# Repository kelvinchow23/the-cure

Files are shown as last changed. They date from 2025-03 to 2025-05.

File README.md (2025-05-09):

# the cure - a UV curing module for well plates



## Purpose
The main function of the curing module is for photopolymerization of a sample using a [UV flood lamp](https://www.amazon.ca/Everbeam-365nm-50W-Black-Light/dp/B08635F9CX/?th=1), intended for samples in a well plate. 
Since UV light poses safety risks, the module includes a motorized tray that slides in and out of a fully enclosed housing. This shields users and the surrounding environment from exposure during operation.
The module is intended to integrate into an automated workflow where a robot arm can pick and place well plates into the box for curing.

## Requirements
- **Microcontroller:** Raspberry Pi Pico W running MicroPython. Honestly, the firmware is very simple and can be adapted to other controllers. It's a matter of controlling 2 digital IO pins for turning on/off relays.
- **Host Computer:** Required to upload firmware and communicate via USB serial. The Pico could potentially operate standalone (e.g., over MQTT), but you’ll still need a computer to flash it initially.
- **Power Source:** Build instructions are for 120VAC (standard NEMA 5-15 plug).
- **Lamp:** The UV lamp has an on/off switch — make sure it is switched *on* for operation.

## Build Overview

This repository includes a three-part guide:
1. **Electronics:** Build and test the electrical components. Instructions are in the `/electrical` folder. 
2. **Mechanical Assembly:** Build instructions for the mechanical housing are in the `/mechanical` folder. 
3. **Firmware & Control:** Use the provided scripts (or your own) to control the module. See **Module Operation** below for operation. 

## Module Operation

The `/scripts` folder contains two key scripts.  
The main firmware script, `UV_module.py`, is uploaded to the microcontroller and provides three core functions:

1. **`move_wellplate_out()`** – Extends the well plate tray.
2. **`move_wellplate_in()`** – Retracts the well plate tray.
3. **`turn_on_UV(duration)`** – Turns on the UV lamp for a specified duration (in minutes).

These functions can be called directly from the microcontroller or remotely via a host computer using tools like `mpremote`.

The `UV_module_controller.py` script is designed to be run on a host computer.  
It communicates with the microcontroller over a serial COM port (currently set to `COM4`, but this may need to be updated based on your system).

When executed, the current workflow is as follows:
1. Retract the well plate tray.
2. Cure the sample for 30 seconds.
3. Extend the well plate tray.

## Notes
- Most 3D-printed parts are made from ASA filament, which is more UV-resistant than standard materials. If ASA printing isn't available, use an alternative UV-resistant material for the housing.
- The actuator's 200mm extension matches the UV lamp’s length (~8"). If using a different lamp, adjust the actuator and tray length to suit.  Note that the guide drawer slides must have an extension longer than the actuator's extension. In this case, the drawer slides have an 8" [203.2mm] extension length.
- This module was designed to mount to an M6 breadboard table. If mounting elsewhere, change the hole features in the UVouter base [C5]. STEP and fusion files are [here](https://github.com/kelvinchow23/the-cure/tree/main/mechanical/3D%20prints%20and%20CAD%20files).

---
  
## Future Steps
- **Electronics:** swap out the perfboard electronics with something a bit cleaner.  it's currently using a dpdt relay since the actuonix actuators were intended to use without an external conntroller. I think this can be done cleaner with an H-bridge module or a 2-channel SPDT relay module. It would still be necessary to have the 3rd relay for controlling the lamp.
- **Housing:**.  The outer and inner housing can be merged together.  This was initially done in two steps because initially, there was no thought of how the moudule would be fixed to a table.
- **UV Lamp:** The lamp itself is not characterized well apart from knowing the wavelength.  Intensity and spatial distribution isn't well known. 
- **Mechanical Housing:** Simplify the housing. The base can likely be reduced from two parts to one. Originally, the two-piece base was added to allow mounting to a plate, which might now be unnecessary with design tweaks.

## Revision History
- **Revision A** - Updated: 2025-04-14

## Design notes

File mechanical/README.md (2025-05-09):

## Bill of Materials (BOM)
Refer to the spreadsheet for the full bill of materials. 
- Parts starting with B need to be purchased. 
- Parts starting with C need to be 3D printed (see below for images of the parts). These parts can be found in the [3D prints and CAD files folder](https://github.com/kelvinchow23/the-cure/tree/main/mechanical/3D%20prints%20and%20CAD%20files).
- The part starting with D needs to be assembled (see instructions in the [electrical folder](https://github.com/kelvinchow23/the-cure/tree/main/electrical)).

### 3D Printed Parts

| #   | Part Name               | Part Qty | Revision | Material | Notes                                                   | Picture Link                                          |
|-----|--------------------------|----------|----------|----------|---------------------------------------------------------|-------------------------------------------------------|
| C1  | Tray                     | 1        | A        | ASA      |  4X M4 heat sets, 4X M3 heat sets                       |   |
| C2  | Actuator Bracket          | 1        | A        | PLA      | Print with any filament, 5X M4 heat sets                |  |
| C3  | Tray Insert              | 1        | A        | ASA      |                                                         |   |
| C4  | Electronics Mounting Plate| 1        | A        | PLA      | Print with any filament, 6X M3 heat sets                | |
| C5  | UV Outer Base            | 1        | A        | ASA      | This is big, split if necessary                        ||
| C6  | Shield                   | 1        | A        | ASA      |                                                       |   |
| C7  | UV Base Lid              | 1        | A        | ASA      |                                                         | |
| C8  | UV Inner Base            | 1        | A        | ASA      | 12X M4 heat sets, 4X M3 heat sets                      | |
| C9  | Back Connector Panel     | 1        | A        | ASA      | 1X M4 heat sets, 2X M3 heat sets                       |  |

*ASA is more UV resistant. Non-ASA parts can be printed with any filament.*

## Tools
- Soldering iron (for soldering and heat sets)
- screwdrivers
- Allan keys
- adjustable wrench
- wire stripper/cutter/crimper
- multimeter
- computer to upload scripts

## Assembly Instructions

Refer to the assembly insturctions document for the build guide.

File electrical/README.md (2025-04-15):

# ⚡ Electrical Components Testing

Before assembling the box, it's a good idea to verify that the electronics function as expected. There are two output devices to test:

1. **Linear Actuators**  
   Verify that the two actuators can extend and retract, and that they are controllable via a GPIO pin on a microcontroller.

2. **AC Relay**  
   Confirm that the AC relay clicks (indicating switching) when triggered by a GPIO pin from a microcontroller.

---

## 🧾 Bill of Materials (BOM)

| #    | Part Description                    | QTY | Vendor   | Vendor/Mfr Part #       | Notes / Link                                                              |
|------|-------------------------------------|-----|----------|--------------------------|---------------------------------------------------------------------------|
| A1   | Raspberry Pi Pico WH (RP2040)       | 1   | Digikey  | SC0919                   | Could substitute with another microcontroller                            |
| A2   | DPDT Relay, 12V, 5V Coil            | 1   | Digikey  | J104B2C12VDC.15S         | Also available from Actuonix (same part)                                 |
| A3   | NPN Transistor                      | 1   | Digikey  | TIP120                   | Interchangeable with similar-rated parts                                 |
| A4   | Flyback Diode                       | 1   | Digikey  | 1N4004G-T                | Interchangeable with similar-rated parts                                 |
| A5   | 1kΩ Resistor                        | 1   | Digikey  | -                        | Interchangeable with similar-rated parts                                 |
| A6   | Header Pins, 0.1" Pitch             | 9   | Digikey  | PRPC040SACN-RC           | Interchangeable with similar-rated parts                                 |
| A7   | 3.2" x 2" Protoboard                | 1   | Digikey  | DKS-SOLDERBREAD-02       | —                                                                         |
| A8   | AC Relay (3.3V Coil)                | 1   | Digikey  | 103020005                | Interchangeable with similar-rated parts                                 |
| A9   | Grove 4-Pin Female Jumper           | 1   | Digikey  | 110990028                | —                                                                         |
| A10  | 100mm Stroke Linear Actuator, 12VDC | 2   | Actuonix | L16-100-63-12-S          | [Link](https://www.actuonix.com/l16-100-63-12-s)                          |
| A11  | 12VDC Power Supply                  | 1   | Actuonix | dcpowersupply            | Can use alternative 12V supply for testing                                |
| A12  | USB Micro-B to USB-A Cable          | 1   | Digikey  | DH-20M50057              | Interchangeable with similar-rated parts                                 |

---

## 🧰 Wiring Diagram

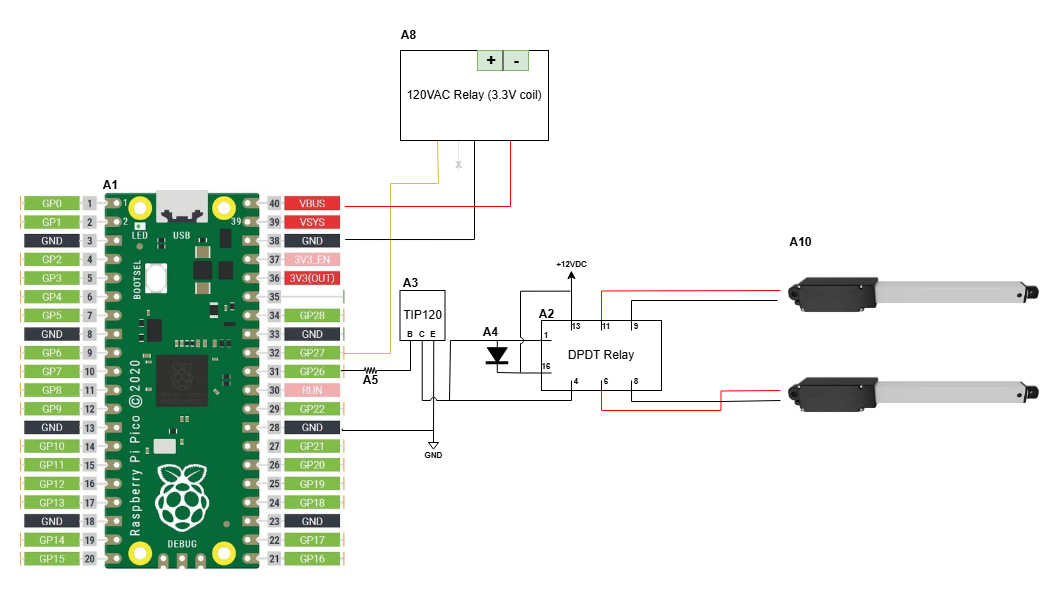
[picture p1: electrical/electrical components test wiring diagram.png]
Wiring Diagram
  
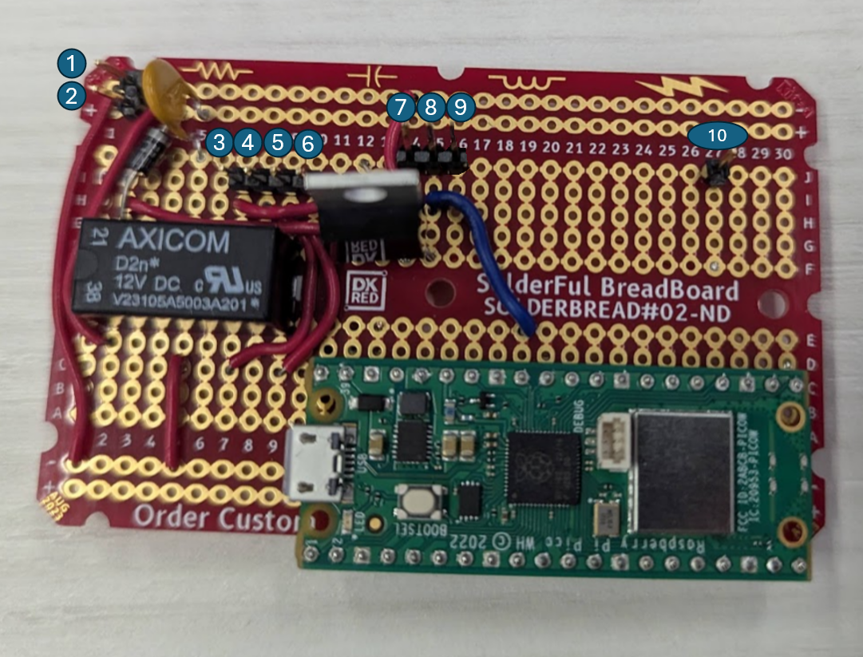
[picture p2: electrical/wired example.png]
Physical Example


- The diagram outlines the setup. The two relays—DC (for actuators) and AC (for a lamp)—can be tested independently.
- You don't need to connect the output terminals of the AC relay yet; a click is sufficient for now.
- A fuse is shown in the diagram connecting V+ to the relay. You can replace this with a jumper wire for testing.
- Wiring on the underside of the protoboard may not be visible in the physical photo.

---

## 🧪 Build & Test Instructions

1. Gather the components listed in the BOM. Substitutes are generally acceptable.
2. Solder components **A1–A6** onto the **A7** protoboard, following the wiring diagram.
   - **Pins 1–2**: 12V Power Supply (V+ and GND)
   - **Pins 3–6**: Actuator outputs (reverse polarity to change direction)
   - **Pins 7–9**: Grove connector to external relay
   - **Pin 10**: external 5V power input (not required if the pico is powered via USB. This will be necessary if it's a standalone module)
3. Connect the linear actuators to pins 3–6. Confirm they move **together**.
4. Connect the AC relay module to pins 7–9 via the Grove jumper. The white cable is not connected.
5. Power the board with a 12V supply through pins 1–2.
6. Connect the Raspberry Pi Pico to your computer using the USB cable.
7. Flash the Pico with **MicroPython firmware**.
8. Upload and run the script `the_cure_electrical_test.py`.
9. The test script will run the following loop:
   - a. Extend actuators  
   - b. Delay: 15 seconds  
   - c. Retract actuators  
   - d. Delay: 10 seconds  
   - e. Turn relay ON (click)  
   - f. Delay: 5 seconds  
   - g. Turn relay OFF  
   - h. Delay: 3 seconds

✅ If the actuators cycle correctly and you hear the relay click, the electronics are working. You can now proceed with the mechanical assembly.

> ⚠️ If actuators **start by retracting**, reverse their polarity or adjust the code.

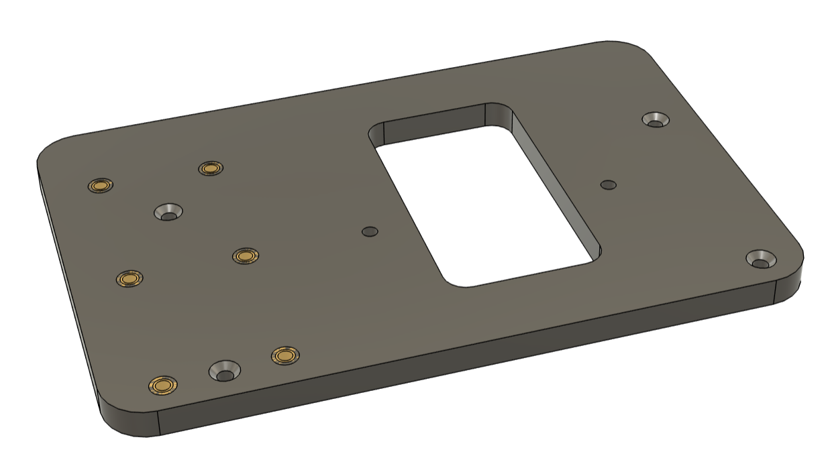
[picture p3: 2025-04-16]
mechanical/3D prints and CAD files/png/electronics mounting plate RevA.png

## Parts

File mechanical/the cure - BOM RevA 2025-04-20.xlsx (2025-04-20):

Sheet: the cure BOM
the cure BOM
Purchased Parts
# | Part Name | Quantity | Vendor | Vendor/Mfr Part # | Unit Cost (USD) | Unit Cost (CAD) | Total Cost (CAD) | Notes
B1 | #8-32 BH screw, 5in L, steel | 1 | McMaster Carr | 90272A053 | $1.05 | $1.51 | $1.51
B2 | M3 BH screw, 6mm L, SS | 4 | McMaster Carr | 92095A179 | $0.06 | $0.08 | $0.34
B3 | M4 BH screw, 6mm L, SS | 18 | McMaster Carr | 92095A188 | $0.12 | $0.17 | $3.14
B4 | M3 FH screw, 10mm L, SS | 6 | McMaster Carr | 92125A130 | $0.07 | $0.11 | $0.63
B5 | M3 standoff, 10mm L, M-F, nylon | 8 | McMaster Carr | 95783A001 | $2.49 | $3.59 | $28.68
B6 | M3 BH screw, 10mm L, SS | 2 | McMaster Carr | 92095A182 | $0.07 | $0.10 | $0.21
B7 | M4 set screw, 6mm L, steel, nylon tip | 4 | McMaster Carr | 94095A110 | $1.72 | $2.48 | $9.91
B8 | M3 FH screw, 6mm L, SS | 2 | McMaster Carr | 92125A126 | $0.06 | $0.09 | $0.18
B9 | M3 FH screw, 20mm L, SS | 4 | McMaster Carr | 92125A136 | $0.13 | $0.19 | $0.74
B10 | M4 BH screw, 10mm L, SS | 4 | McMaster Carr | 92095A190 | $0.09 | $0.14 | $0.54
B11 | M4 BH screw, 15mm L, SS | 1 | McMaster Carr | 92095A125 | $0.09 | $0.13 | $0.13
B12 | M4 to #8-32 thread adapter, 1.5in L, steel | 1 | McMaster Carr | 91082A110 | $11.57 | $16.66 | $16.66
B13 | Cable tie mount, 19mm base, nylon | 1 | McMaster Carr | 7566K104 | $0.08 | $0.12 | $0.12
B14 | M4 locknut, 316 SS, nylon insert | 1 | McMaster Carr | 94205A230 | $0.15 | $0.21 | $0.21
B15 | threadlocker, medium strength | A/R | McMaster Carr | 91458A112 | $0.00 | $0.00 | $0.00
B16 | UV flood lamp, 365nm, 50W | 1 | Amazon | B08635F9CX | $0.00 | $59.99 | $59.99 | https://www.amazon.ca/Everbeam-365nm-50W-Black-Light/dp/B08635F9CX/?th=1
B17 | Drawer slides, 8in, pair | 1 | Amazon | B08VD84GV9 | $0.00 | $14.99 | $14.99 | https://www.amazon.ca/Laigoo-Extension-Bearing-Cabinet-Drawers/dp/B08VD84GV9
B18 | 5/12V dual power supply | 1 | Digikey | 1866-3983-ND | $0.00 | $16.89 | $16.89
B19 | USB-micro B cable, panel mount, 1ft | 1 | Digikey | 1528-1786-ND | $0.00 | $4.95 | $4.95
B20 | Power entry connector, C14, Panel mount | 1 | Digikey | 486-1963-ND | $0.00 | $10.47 | $10.47
B21 | cable ties | A/R | Digikey | 2162-AL-04-18-9-M-ND | $0.00 | $0.00 | $0.00
B22 | M3 heat set inserts | 20 | Digikey | 2254-M30X170C-ND | $0.00 | $0.34 | $6.80
B23 | M4 heat set inserts | 22 | Digikey | 5519-TH-M40-SV-ND | $0.00 | $0.16 | $3.52
B24 | Linear actuators, L-16-S, 63:1, 100mm stroke | 2 | Actuonix | L16-100-63-12-S | $70.00 | $100.80 | $201.60
B25 | Actuator mounting bracket | 1 | Actuonix | - | $0.00 | $0.00 | $0.00 | included with Actuonix actuator
B26 | Cable, power, 5-15P to C13, 1m | 1 | Digikey | 839-1187-ND | $0.00 | $4.11 | $4.11
B27 | Double sided tape | A/R | Amazon | B00OXVG9FW | $0.00 | $0.00 | $0.00 | https://www.amazon.ca/Gorilla-Tape-6065001-Mounting-Clear/dp/B00OXVG9FW
For custom cables
# | Part Name | Quantity | Vendor | Vendor/Mfr Part # | Unit Cost (USD) | Unit Cost (CAD) | Total Cost (CAD) | Notes
B28 | jumper wires, F-F, 12in L, 20 pack | 1 | Digikey | 1528-1960-ND | $0.00 | $3.95 | $3.95 | need 3 jumpers
B29 | power cord, 18 AWG, C-13 to bare leads, 2m | 1 | Digikey | 1175-800-1809-2-SJT0-BL-00200-1-ND | $0.00 | $5.42 | $5.42
B30 | connector, spade, #6 stud, 22-26 AWG | 3 | Digikey | A27435-ND | $0.00 | $0.67 | $2.01 | couldn't find a 28 AWG connector, soldered the wire to this connector
B31 | connector, spade, #6 stud, 16-22 AWG | 6 | Digikey | A1063-ND | $0.00 | $0.35 | $2.10
B32 | connector, faston, .25in width, 18-22 AWG | 3 | Digikey | WM18764-ND | $0.00 | $0.24 | $0.72
B33 | connector, wago, 2 position, 12-24 AWG | 1 | Digikey | 2946-221-412-ND | $0.00 | $0.54 | $0.54
 |  |  |  |  |  | SUM | $401.06
Custom Parts
3D printed parts
# | Part Name | Part Qty | Revision | Material* |  |  |  | Notes
C1 | tray | 1 | A | ASA
C2 | actuator_bracket | 1 | A | PLA |  |  |  | print with any filament 5X M4 heat sets
C3 | tray insert | 1 | A | ASA
C4 | electronics mounting plate | 1 | A | PLA |  |  |  | print with any filament 6X M3 heat sets
C5 | uv outer base | 1 | A | ASA |  |  |  | this is big, split if necessary
C6 | shield | 1 | A | ASA |  |  |  | 4X M4 heat sets, 4X M3 heat sets
C7 | uv base lid | 1 | A | ASA
C8 | uv inner base | 1 | A | ASA |  |  |  | 12X M4 heat sets, 4X M3 heat sets
C9 | back connector panel | 1 | A | ASA |  |  |  | 1X M4 heat sets, 2X M3 heat sets
 |  |  |  | *ASA is more UV resistant. Non ASA parts can be printed in anything
Electronics
# | Part Name | Part Qty | Revision |  |  |  |  | Notes
D1 | electronics control board | 1 | A |  |  |  |  | Refer to the documentation in the electrical folder for BOM, build, and test instructions

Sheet: revision history
Revision | Change Description | Date
A | Initial Release | 2025-04-16

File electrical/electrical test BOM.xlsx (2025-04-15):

Electrical Components Test BOM
# | Part Description | QTY | Vendor | Vendor/Mfr Part # | Link/Notes
A1 | RASPBERRY PI PICO WH RP2040 | 1 | Digikey | SC0919 | could probably use a different microcontroller
A2 | DPDT Relay, 12V, 5V Coil | 1 | Digikey | J104B2C12VDC.15S | This can be bought from Actuonix as well, it's the same part
A3 | NPN Transistor | 1 | Digikey | TIP120 | Interchangeable with similar-rated parts.
A4 | Flyback Diode | 1 | Digikey | 1N4004G-T | Interchangeable with similar-rated parts.
A5 | 1kΩ resistor | 1 | Digikey | - | Interchangeable with similar-rated parts.
A6 | header pins, 0.1" pitch | 10 | Digikey | PRPC040SACN-RC | Interchangeable with similar-rated parts.
A7 | 3.2" x 2" protoboard | 1 | Digikey | DKS-SOLDERBREAD-02
A8 | AC Relay (3.3V Coil) | 1 | Digikey | 103020005 | Interchangeable with similar-rated parts.
A9 | Grove 4 pin female jumper |  | Digikey | 110990028
A10 | 100mm stroke linear actuator, 12VDC | 2 | Actuonix | L16-100-63-12-S | https://www.actuonix.com/l16-100-63-12-s
A11 | 12VDC Power Supply | 1 | Actuonix | dcpowersupply | Another power supply is used in the actual module but this can be used for a quick test
A12 | USB micro-B to USB A cable | 1 | Digikey | DH-20M50057 | Interchangeable with similar-rated parts.

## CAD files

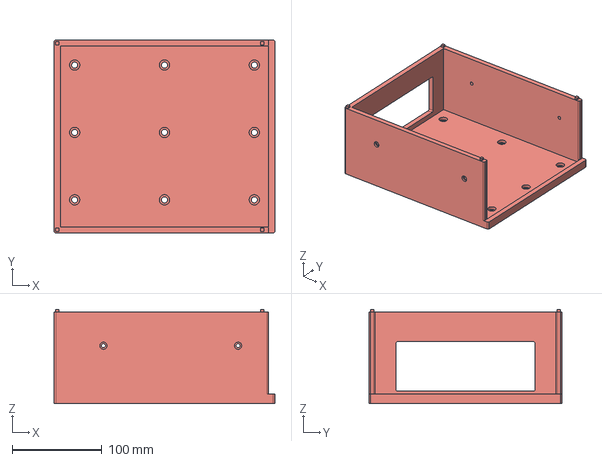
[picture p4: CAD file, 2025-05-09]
mechanical/3D prints and CAD files/step/uv outer base RevA.step
246.0 x 215.0 x 105.0 mm

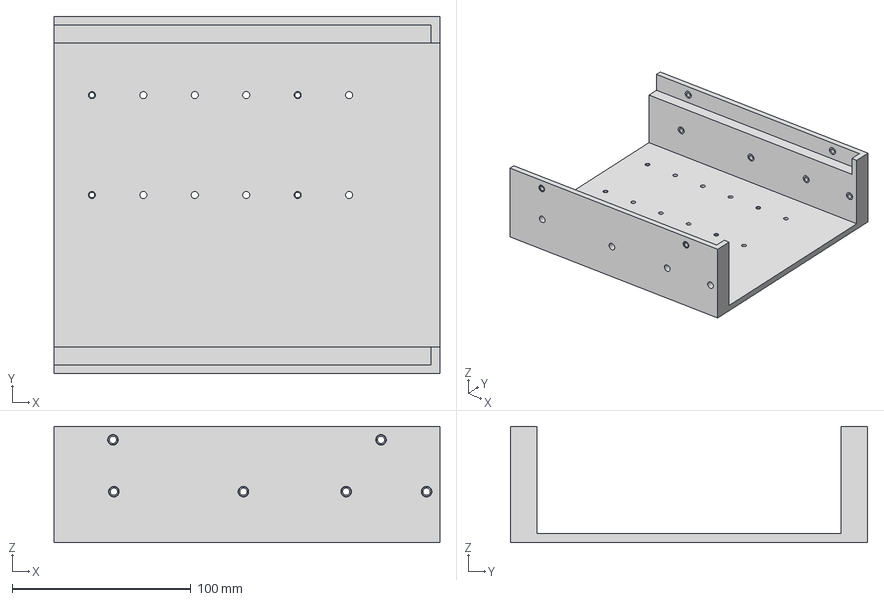
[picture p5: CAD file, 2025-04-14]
mechanical/CAD files/uv curing housing v71.step
216.0 x 200.0 x 65.0 mm
94180A331_NO THREADS_Tapered Heat-Set Inserts for Plastic x 8
94180A351_NO THREADS_Tapered Heat-Set Inserts for Plastic_1 x 6
94180A351_NO THREADS_Tapered Heat-Set Inserts for Plastic x 6

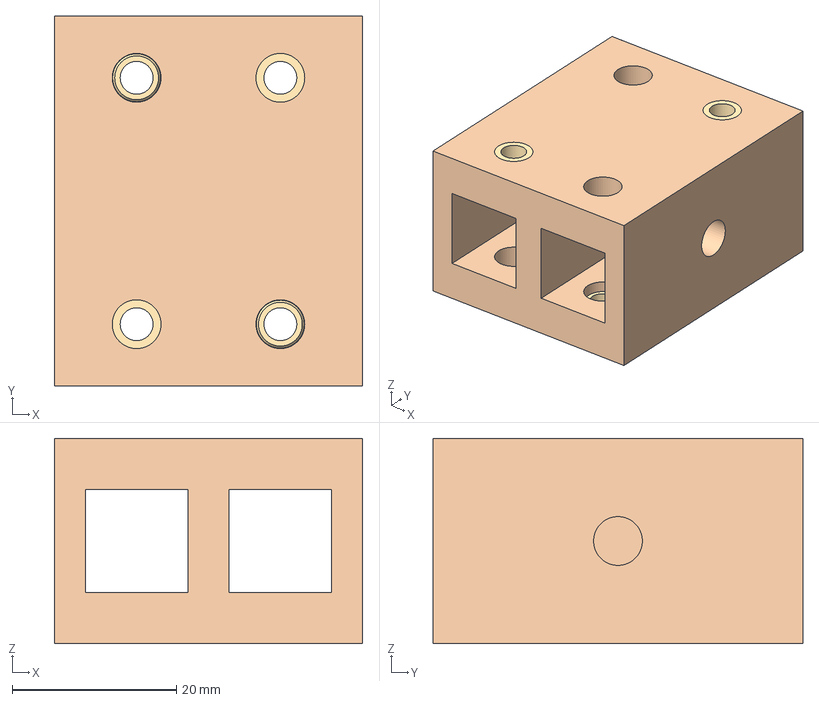
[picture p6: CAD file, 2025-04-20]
mechanical/3D prints and CAD files/step/actuator bracket RevA.step
37.5 x 45.0 x 25.0 mm
94180A351_NO THREADS_Tapered Heat-Set Inserts for Plastic x 5

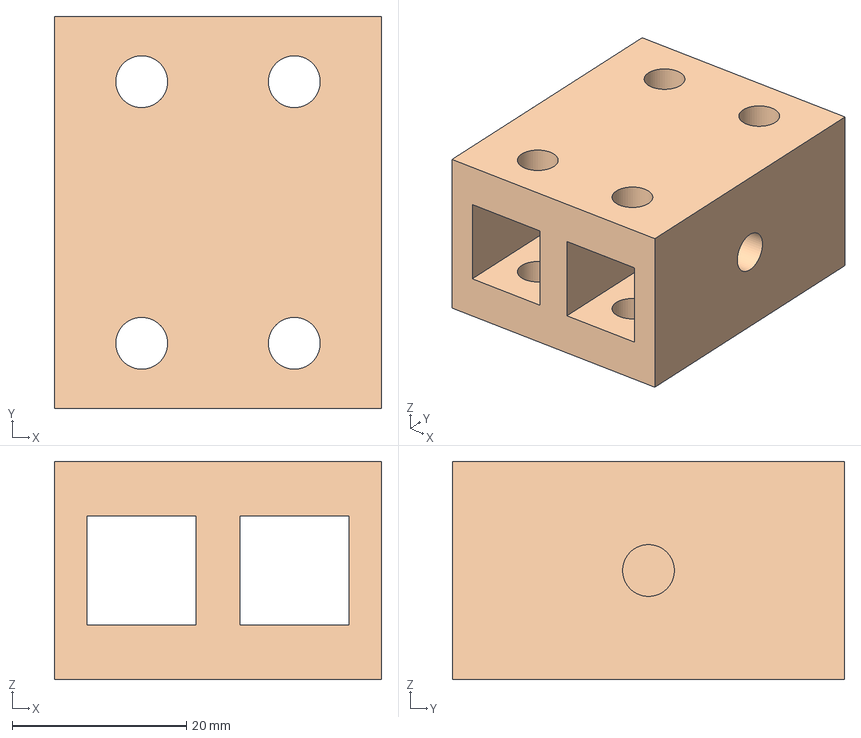
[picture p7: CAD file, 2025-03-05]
mechanical/CAD files/actuator_bracket v26.step
37.5 x 45.0 x 25.0 mm

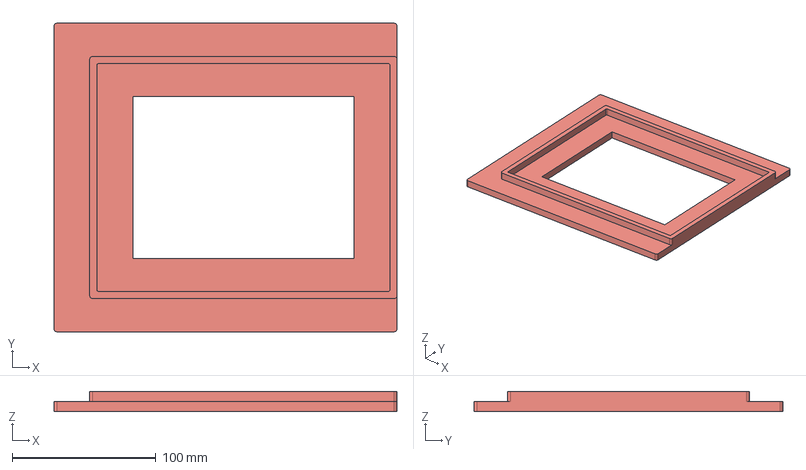
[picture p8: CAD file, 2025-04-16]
mechanical/3D prints and CAD files/step/uv base lid RevA.step
239.0 x 215.0 x 14.0 mm

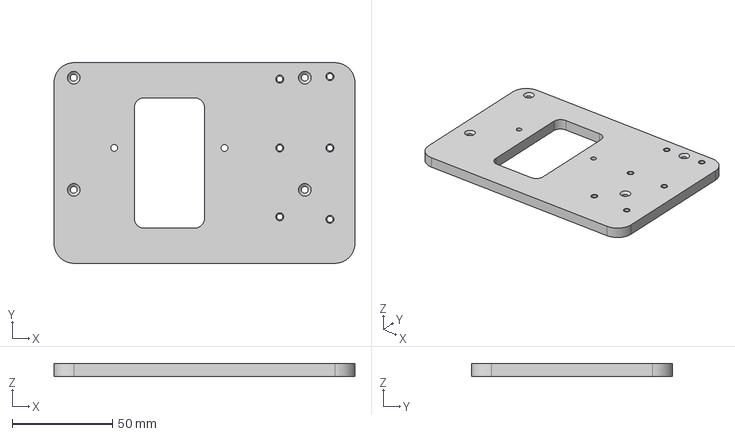
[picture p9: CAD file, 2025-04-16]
mechanical/3D prints and CAD files/step/electronics mounting plate RevA.step
150.0 x 100.0 x 6.35 mm
94180A331_NO THREADS_Tapered Heat-Set Inserts for Plastic x 6

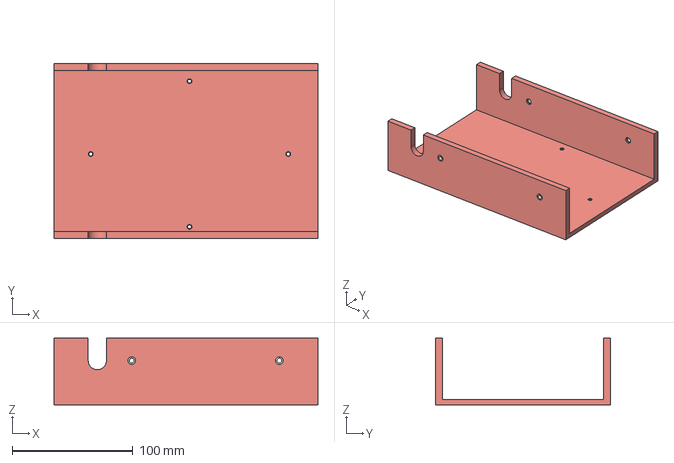
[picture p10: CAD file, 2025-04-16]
mechanical/3D prints and CAD files/step/tray RevA.step
218.3 x 145.0 x 55.0 mm
94180A331_NO THREADS_Tapered Heat-Set Inserts for Plastic x 4
94180A351_NO THREADS_Tapered Heat-Set Inserts for Plastic x 4

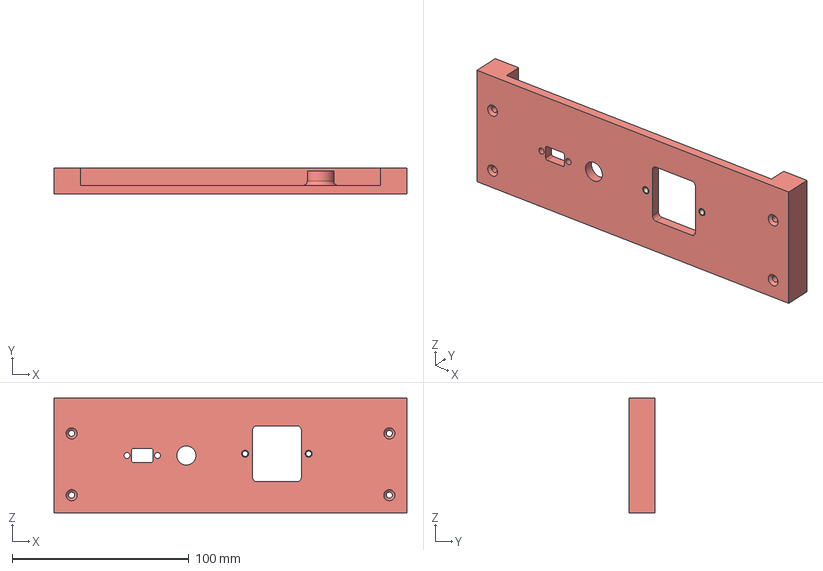
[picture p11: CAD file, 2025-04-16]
mechanical/3D prints and CAD files/step/back connector panel RevA.step
200.0 x 15.0 x 65.0 mm
94180A331_NO THREADS_Tapered Heat-Set Inserts for Plastic x 2
94180A351_NO THREADS_Tapered Heat-Set Inserts for Plastic

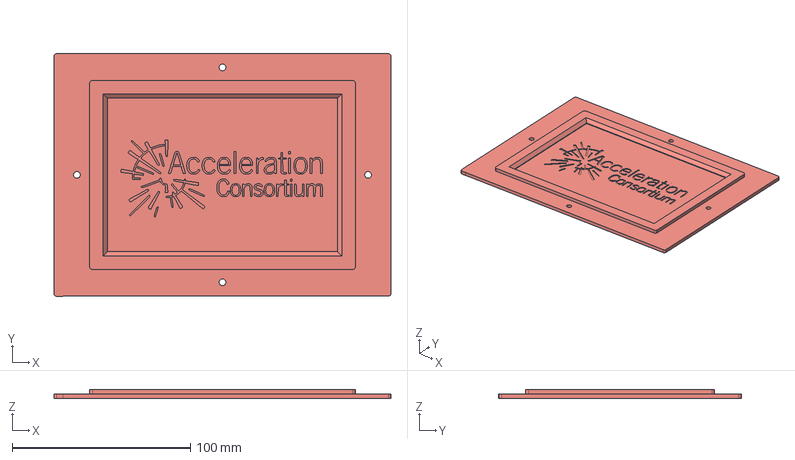
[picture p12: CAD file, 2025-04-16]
mechanical/3D prints and CAD files/step/tray insert RevA.step
189.0 x 136.1 x 5.00 mm

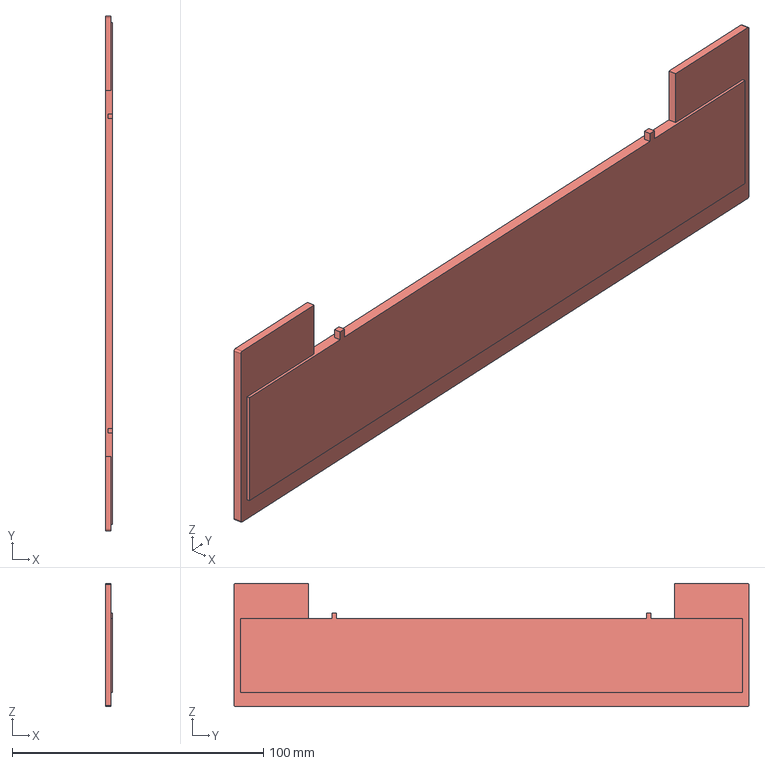
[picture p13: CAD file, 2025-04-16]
mechanical/3D prints and CAD files/step/shield RevA.step
2.90 x 205.0 x 49.0 mm

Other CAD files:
mechanical/3D prints and CAD files/step/uv inner base RevA.step
mechanical/3D prints and CAD files/assembly_the_cure RevA 2025-05-09.f3z
mechanical/3D prints and CAD files/stl/actuator bracket RevA.stl
mechanical/3D prints and CAD files/stl/back connector panel RevA.stl
mechanical/3D prints and CAD files/stl/electronics mounting plate RevA.stl
mechanical/3D prints and CAD files/stl/shield RevA.stl
mechanical/3D prints and CAD files/stl/tray RevA.stl
mechanical/3D prints and CAD files/stl/tray insert RevA.stl
mechanical/3D prints and CAD files/stl/uv base lid RevA.stl
mechanical/3D prints and CAD files/stl/uv inner base RevA.stl
mechanical/3D prints and CAD files/stl/uv outer base RevA.stl

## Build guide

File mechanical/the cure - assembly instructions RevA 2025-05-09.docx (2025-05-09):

# the cure - assembly instructions

Rev: A

Date drafted:2025-05-09

Drafted by: Kelvin Chow

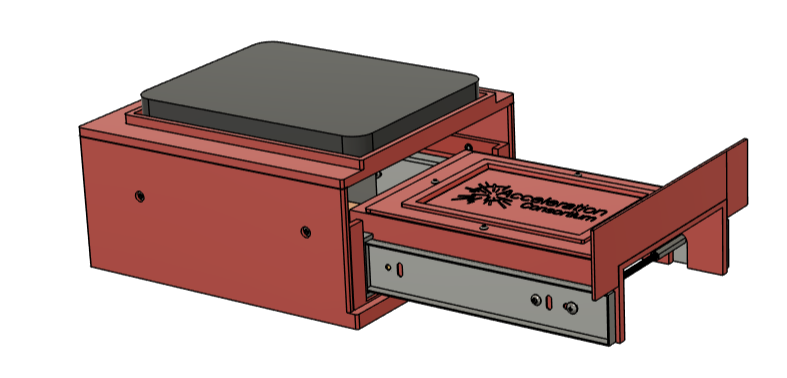
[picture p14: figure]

## Section 1: Print Parts and Install Heat-Set Inserts

1. 3D print all 9 parts (1X C1-C9,). STL files are located here (https://github.com/kelvinchow23/the-cure/tree/main/mechanical/3D%20prints%20and%20CAD%20files/stl)
2. Install heat set inserts for the following:
  - Tray [C1]
    i. m3 inserts on the top [4X B22]
    ii. m4 inserts on the sides [4X B23]
  - actuator bracket [C2]
    iii. m4 inserts as shown below [5X B23].
  - electronics mounting plate [C4]
    iv. m3 inserts [6X B22].
  - UV inner base [C6]
    v. m3 inserts on the bottom and back [8X B23]
    vi. m4 inserts on the sides [12X B23]. Note: these need to be installed from the outside and pushed all the way flush to the inner surface
  - back connector panel [C9]
    vii. m3 inserts [2X B22]
    viii. m4 insert [1X B23].

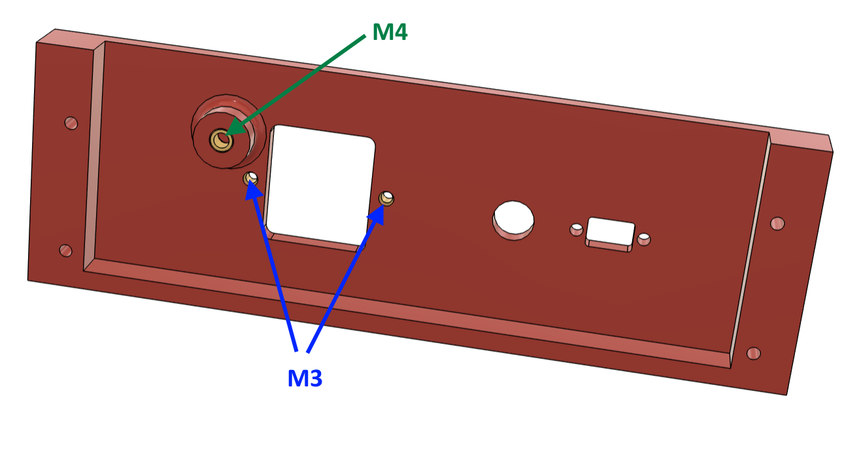
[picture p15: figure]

## Section 2: Build Custom Cables

There are 5 custom cables to build.

Cable # | From | To | Description
E1 | WAGO + DC power (AC L + GND) | UV lamp | AC receptacle for UV lamp
E2 | Power entry module | Power supply (AC) | Feeds 120VAC to the DC power supply
E3 | Power supply (DC terminals) | Electronics board | Delivers 5V/12V to custom electronics
E4 | WAGO | AC relay | Neutral wire to relay
E5 | Power supply (AC neutral) | WAGO | Neutral line to WAGO connector

3. Build cable E1: UV lamp receptacle
  - Take the power cord [B29] and measure 50cm from the connector and cut it. (Do not throw away the cable ends as they will be used for cable E2)
  - On the cut end, remove about 6cm off the black jacket and trim each of the 3 wires about 1cm.
  - Crimp on spade connectors [2X B31] to the green and white wires.

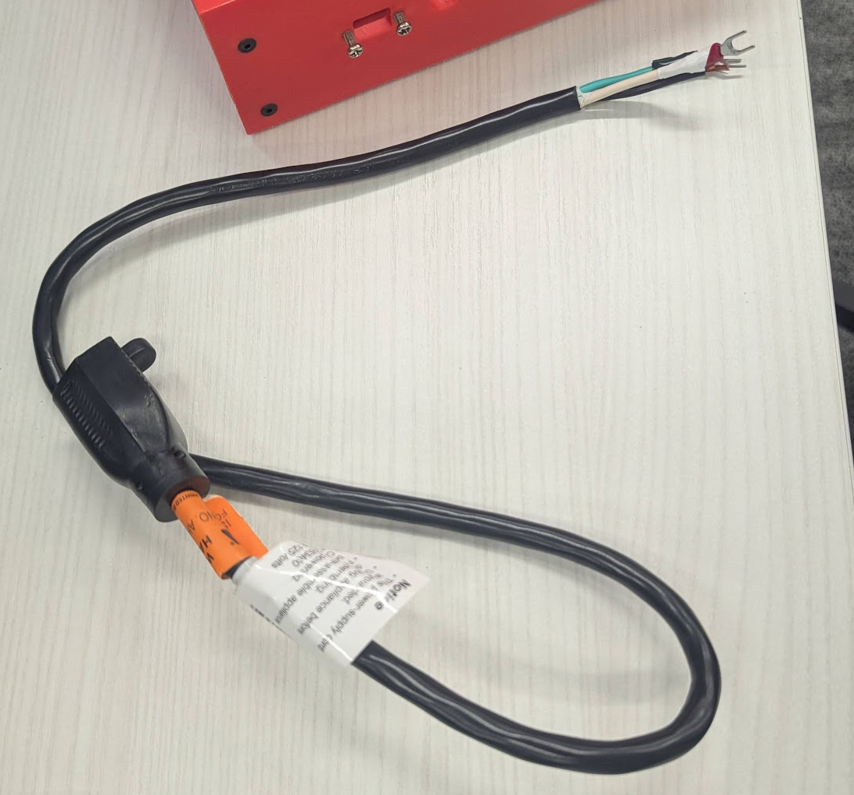
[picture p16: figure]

4. Build cable E2: Power entry to power supply
  - With the excess cable from the previous step, cut a length of 15cm.
  - Strip off the entire black jacket to get 3 wires
  - For all cables on both ends (6 total), strip about 1cm
  - For all cables, crimp a Faston connector [3X B32 on one end and crimp a spade connector [3X B31] on the other end.
  - Connect the quick disconnect end of these wires to the back of the power entry connector [1X B20] as shown below. Connectors should snap in. The connector should be labelled N and ground. Black goes to top connection, white goes to N, and green goes to ground.
5. Build cable E3: power supply to electronics

(Note: the image shows a different spade connector; use yellow instead.)

  - Take female jumper wires [3X B28]. These 3 wires will be for 5V, 12V and V-, so ideally you have a colours like black, red, and white.
  - For each wire, measure 20cm from one end of the female header and cut off the end.
  - For each wire, strip the bare end about 1cm.
  - For each wire, crimp on a spade connector [3X B30]. Note that if the crimp is not secure, solder this connection (or find a spade connector that accepts 28 AWG).
6. Build cable E4 and E5: relay neutral cables
  - Take a spool of black 22 AWG stranded wire [B33]. Cut 2 wires, both 25cm in length.
  - For both wires, strip both ends about 1cm. (One of these cables [E5] is complete at this stage)
  - For only one of the wires, crimp a spade connector [1X B31] on one end. This cable is complete [E4].

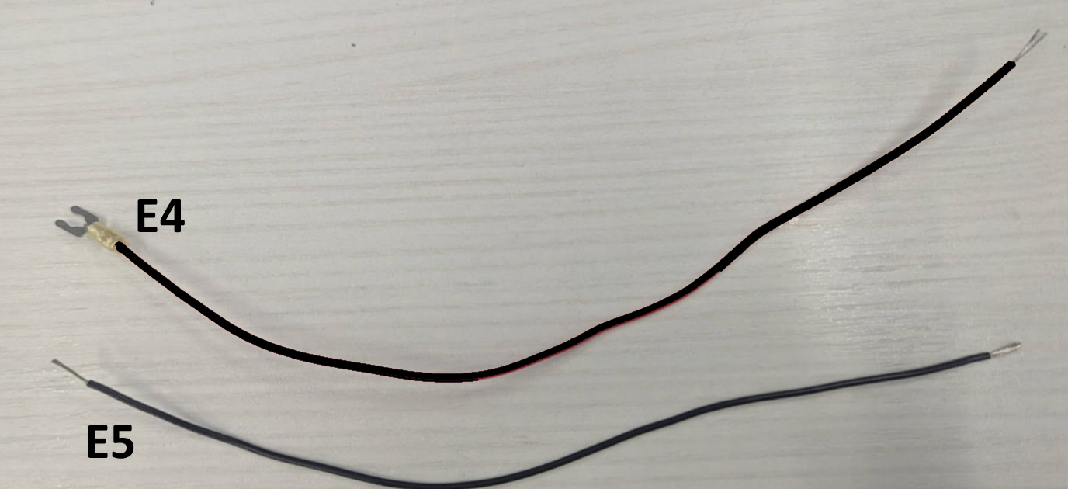
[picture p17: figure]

## Section 3: Assemble the inner base

7. Instal the pair of drawer slides [1X B17] to the inner base [1X C8] with M4x6mm button screws [12X B3]. These rails need to be extended fully to install the screws from the inner face. Note the orientation from the image below. The slides extend away from the heat set inserts on the back panel.
8. Install the power supply [1X B18] to the electronics mounting plate [1XC4] with M3X10mm flat head screws [2X B4]

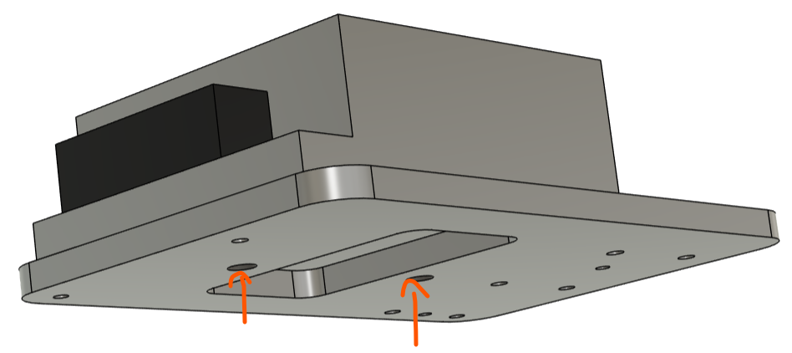
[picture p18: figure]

9. Install the power supply and plate to the inner base using M3x10mm flat head screws [4XB4]. Note the power supplies terminal are facing at the back. They really should be installed with 4 screws, but 2 screws are blocked by the power supply. This design should have been temporary anyways.

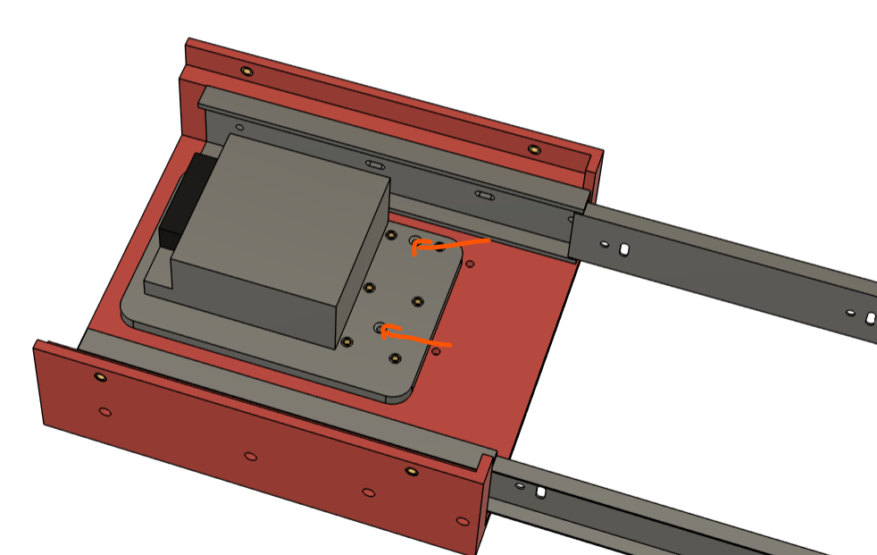
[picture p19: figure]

10. Install nylon standoffs [4X B5] into the electronics mounting plate. Install in the inserts shown below.

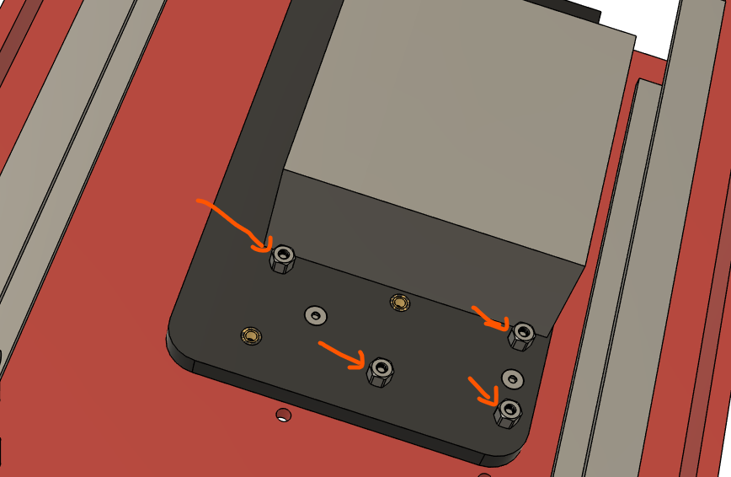
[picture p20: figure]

11. Install the electronics control board [1X D1] onto the standoffs from the previous step. Secure with more standoffs [4X B5] (note in the image below, it is an empty protoboard, it should be populated with components).

## Section 4: Attach actuators to slides

12. Take both actuators [2X B24] and extend them. There are a few ways to do this. The easiest way is to directly connect the actuators to a 12VDC power supply (V+ and V-). If it’s plugged in and the actuators don’t move, reverse the wires to extend.

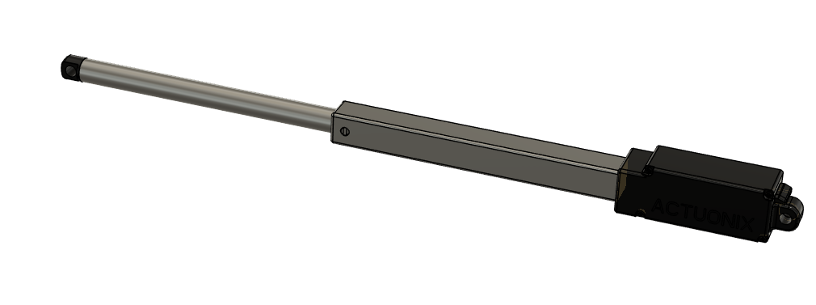
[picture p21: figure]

13. Install the actuator mounting bracket [1X C2] to attach the 2 actuators together. The mounting bracket should slide over the shaft/housing of the actuators. Do this one at a time. Ensure that the bracket is touching the black faces of both actuators as indicated below.

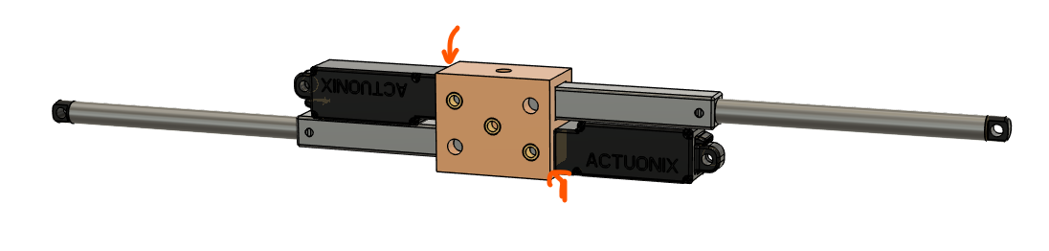
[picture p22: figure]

14. Secure the actuators to the bracket with M4 set screws [4X B7]. Theres should be 2 set screws installed for each actuator, 1 on each side.
15. Install a cable tie mount [1X B13] to the middle hole of the actuator mounting bracket using an M4x6mm screw [1X B3].

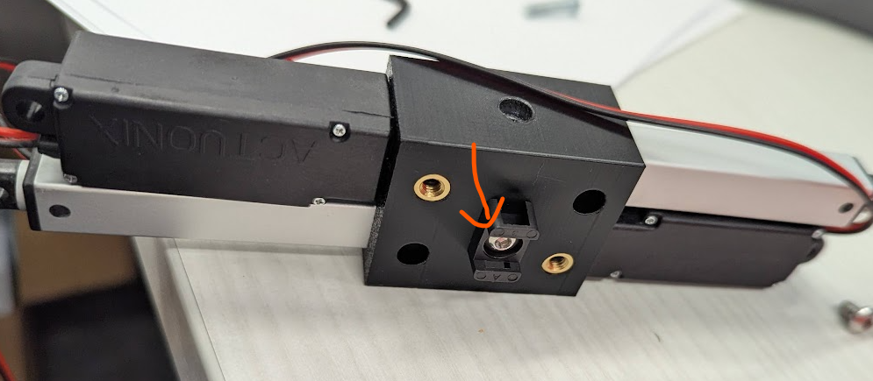
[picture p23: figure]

16. On the right drawer slide, install the #8-32 6in screw [1X B1] and secure with an 8-32 locknut. The Actuonix actuators come with mounting hardware, which includes #8-32 locknuts. Use a different locknut (such as one with a lock washer) for easier assembly. This screw is installed into a slotted hole in the drawer slide, and positioning will need to be adjusted in a later step.
17. Slide the actuator assembly over the long screw. Note the orientation of the assembly from the image below.

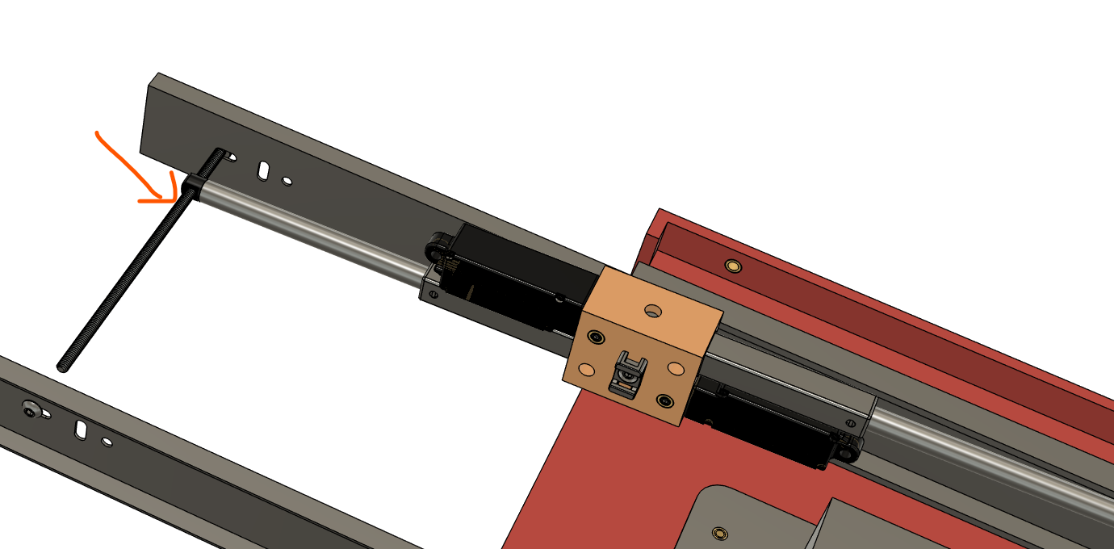
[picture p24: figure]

18. Retract the drawer slides to a position as shown below.

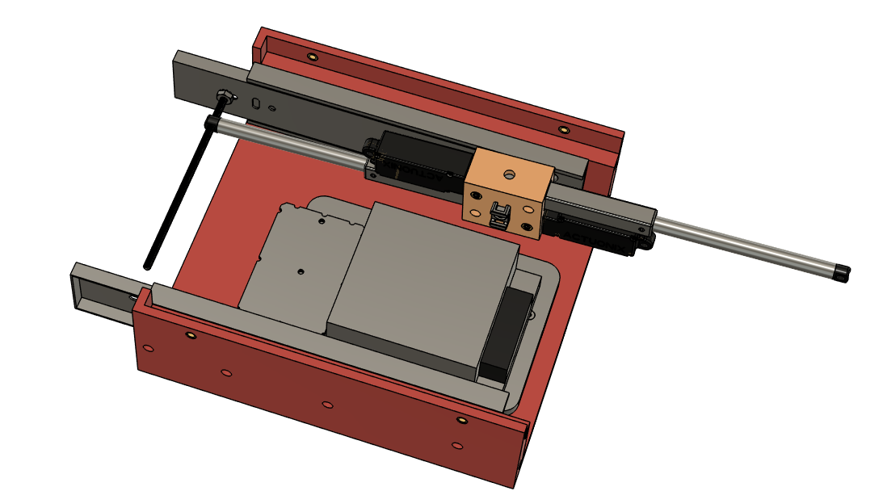
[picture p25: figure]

19. Install the thread adapter [1X B12] on the left side with threadlocker [B15]. Note that the nut on the right side to secure the screw will probably need to be loosened to allow for the thread adapter to be installed. Install the thread adapter so it is touching the left drawer slide’s inner face. Re-tighten the right nut if necessary.
20. Install an M4 x 6mm long screw [1X B3] on the right drawer slide to secure the thread adapter/long screw. Use threadlocker [B15]. After this is installed, ensure that the drawer slide can freely slide in and out. If not, readjust the positioning of the thread adapter.

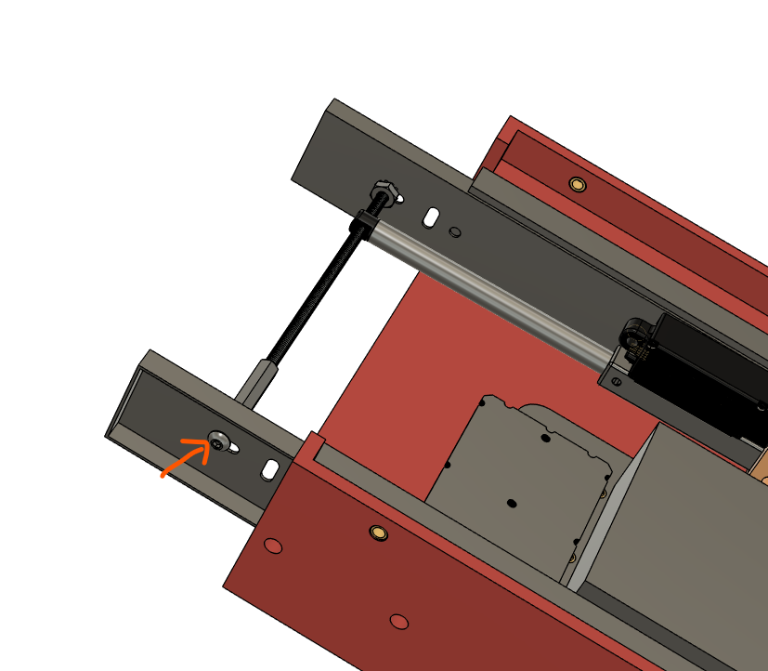
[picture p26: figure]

## Section 5: Install back panel and begin cable wiring

21. Take the back connector panel [1X C9] and install the following components.
  - USB cable [1X B19] on the left side. Secure this with M3x10mm screws [2X B6].
  - Power entry connector [1X B20]. In Section 2, this connector was pre-assembled with 3 cables, cable E2. Feed these cables through the right rectangular cutout and secure with M3 flat head screws [2X B8].
  - The smaller circular cutout in the middle is for the E1 cable that was assembled in section 2. Feed this cable through the hole (missing in the image below).

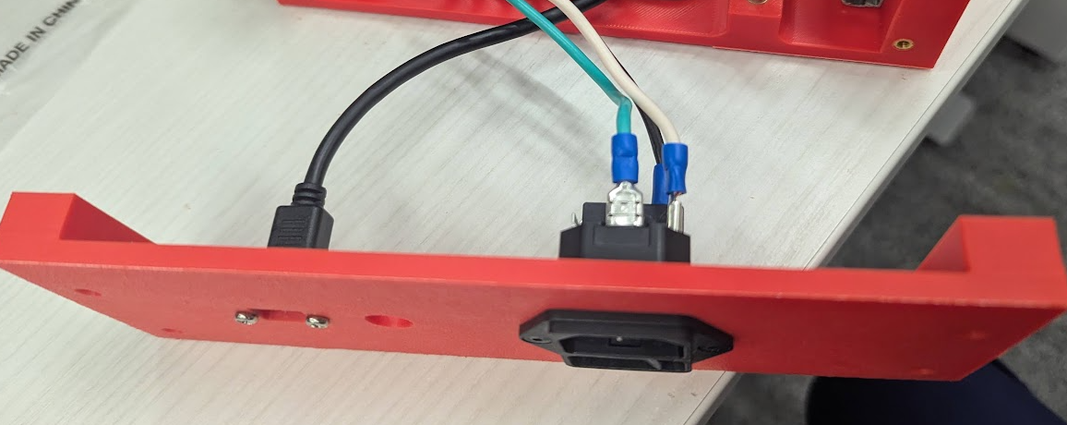
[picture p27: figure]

22. Install the Actuonix mounting bracket [1X B25] using threadlocker and an M4x6mm screw to the back connector panel.

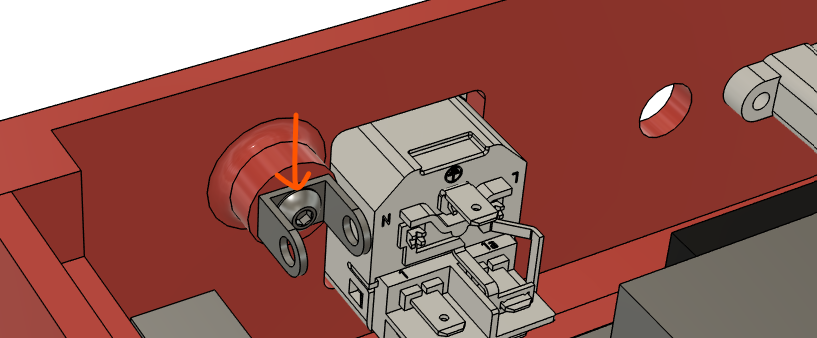
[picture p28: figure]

23. Install the rod end of the actuator to this bracket. Use an M4x15mm screw [1XB11] and a M4 nylon-insert locknut [1X B14].
24. Connect the wires from the 2 actuators to the electronics control board (relay pins). During testing, the polarity of the wires should have been figured out which way to connect them.
25. Route the wires through a cable tie at the centre of the actuator mounting bracket.
26. This step is optional and not shown in the picture below, but it is a very good idea to provide an external way of supply 12VDC to these actuators in case there is a situation where this module or its electronics are damaged/disconnected. What was done after was a 2 pin jumper wire was soldered in parallel to the actuator wires. The other end of the jumper wires were taped down to the 3d printed housing in a location that was accessible for a user after the module was fully built.

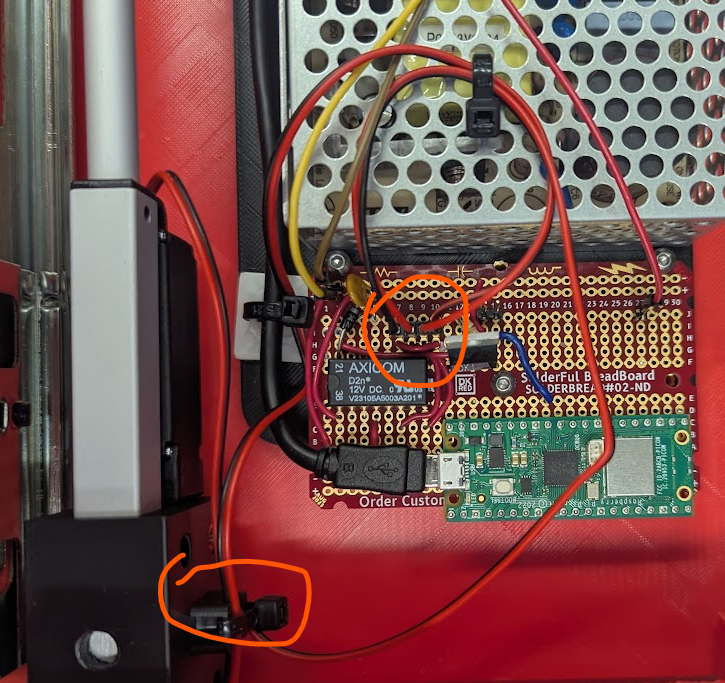
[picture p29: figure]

27. Wire cable E2 from the power entry module to the power supply’s AC terminals. The AC terminals should be on the right side. They should be wired accordingly
- Black to L (Live)
- White to N (Neutral)
- Green to ground symbol

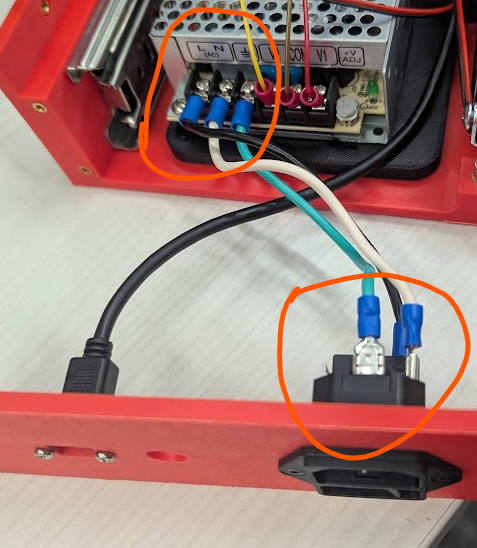
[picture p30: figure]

28. Plug in a power cable [1X B26] to the power connector module and turn it on to test the power supply. A green LED should turn on. If probing the DC terminals with a multimeter, V1/COM should be 5V and V2/COM should be 12V. There is a screw on the right to adjust voltage if necessary.
29. Wire all the electronics together, but this should all be done without the back connector panel installed yet. Refer to the schematic and the image below for general guidance on how to install the power connector module, power supply, electronics control board, and relay. The notes below are probably in chronological order of how it should be wired.

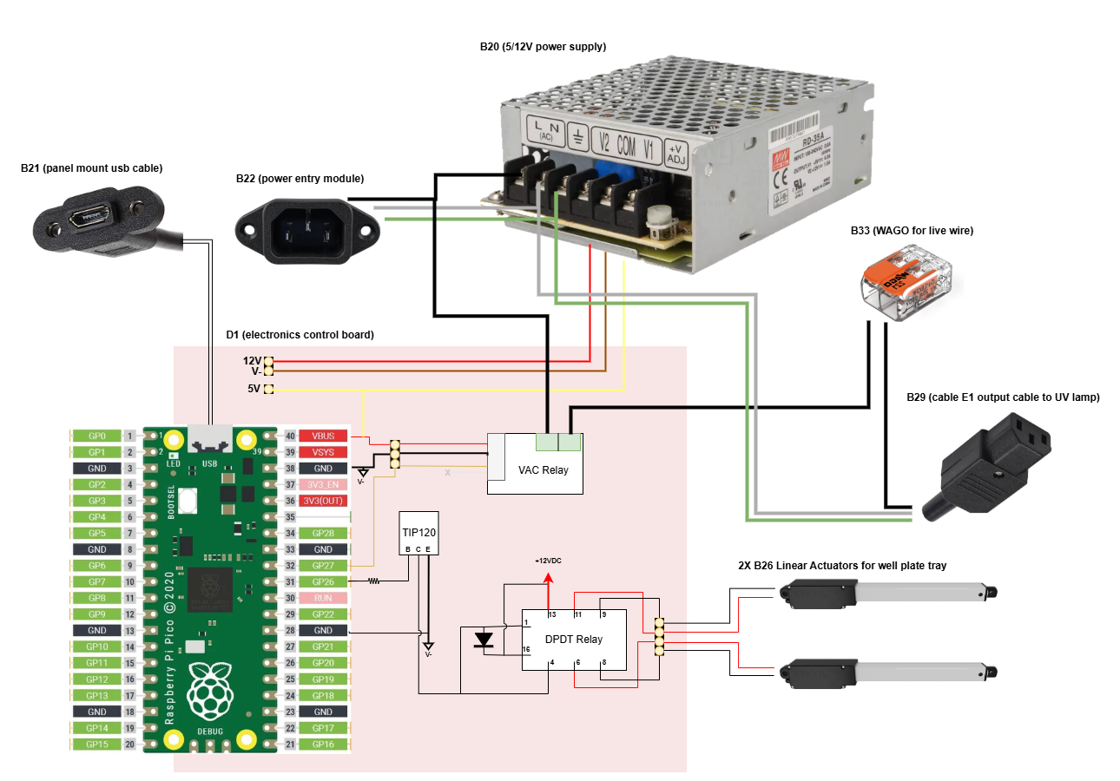
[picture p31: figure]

- For the AC terminals on the power supply, there should be 2 connections on each of the 3 terminals.
  - Live: Black wire from the power connector (cable E2) and cable E4 to the relay. Note that it is red in this picture and in Section 2 (and in the wiring diagram), this wire is black.
  - Neutral: White wire from cable E2 and cable E1.
  - Ground: green wires from cable E2 and cable E1.
- The DC terminals on the power supply connect to the electronics control board to provide power. In he image above,
  - Yellow provides 12V (V2 on the power supply)
  - Brown is the V- rail (COM on the power supply)
  - Red provides 5V to power the pico (V1 on the power supply).
- Connect the micro-USB to the raspberry Pico.
- Wire the relay.
  - The grove wire should connect between the relay to electronics control board.
    - Black connects to ground
    - Red connects to 5V
    - White is not connected
    - Yellow connects to a GPIO pin on the raspberry Pico
  - The AC screw terminals on the relay are interchangeable and connect to:
    - The other end of cable E5.
    - Cable E4.
- On the other end of cable E4 (black wire bare on both ends), connect it to the WAGO connector. The other end should connect to the black wire of cable E1.
30. Once all wiring is complete, secure the relay in the location below. On the backside of that relay, there is double sided tape [B27] that both insulates and secures it to the standoffs/electronics control board.
31. Install the back connector panel with M3x20mm long screw [4X B9].

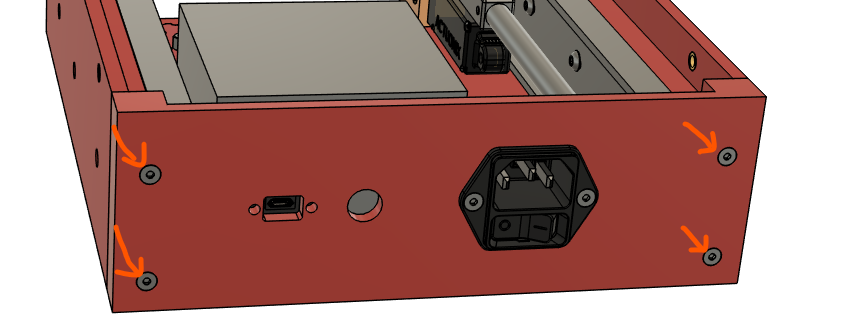
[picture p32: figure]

32. Test that the electronics function as expected.
  - Connect a power cable to the power entry cable. Flip the switch to the ON position.
  - Connect a micro usb-B cable to the back panel connector to a computer
  - Upload the script, UV_module.py to the pico, which can be found [here](https://github.com/kelvinchow23/the-cure/tree/main/scripts). The pico should be running micropython.
  - Note the COM port of the pico.
  - Run the script, UV_module_controller.py. This should loop through the workflow. Check for the following:
    i. When the actuator is fully retracted, the drawer slides should also be fully retracted. If not, adjust the position of the screws securing the actuator to the drawer slide.
    ii. When the relay is switched on or off, an audible click is heard.
33. While testing the actuators, look at the wires when the actuators move. Avoid loose wires dangling and secure them down with cable ties [B21]. Note in the image below the cable ties used to secure the wires. The lone exception is the wires for the actuator, which needs to move. Allow for some slack there, but those wires shouldn’t be taking up vertical space either.

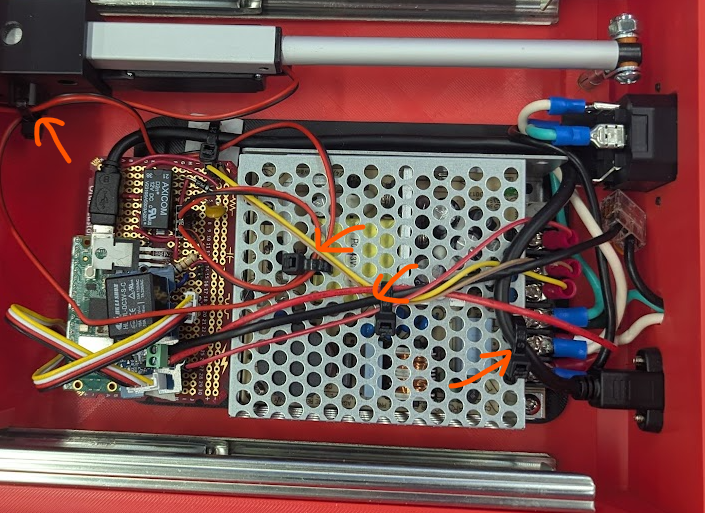
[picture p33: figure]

## Section 6: Install remaining 3D printed parts

34. Extend the actuators fully (either modify the script or run the existing script and shut off the power when the actuator is fully extended).
35. Secure the well plate tray [1X C1] to the drawer slides with M4x6mm screw [4X B3]. Note that there is an issue where the front 2 screws can be installed, but the back 2 screws cannot be. The location circled in blue could be installed from the inside, but the location circled in green could not (blocked by the actuators).
36. Re-run the script to test the movement doesn’t interfere with the wires. If they do, re-secure the wires.
37. Install the tray insert [1X C3] to the well plate tray using M3x6mm screw [4X B2].

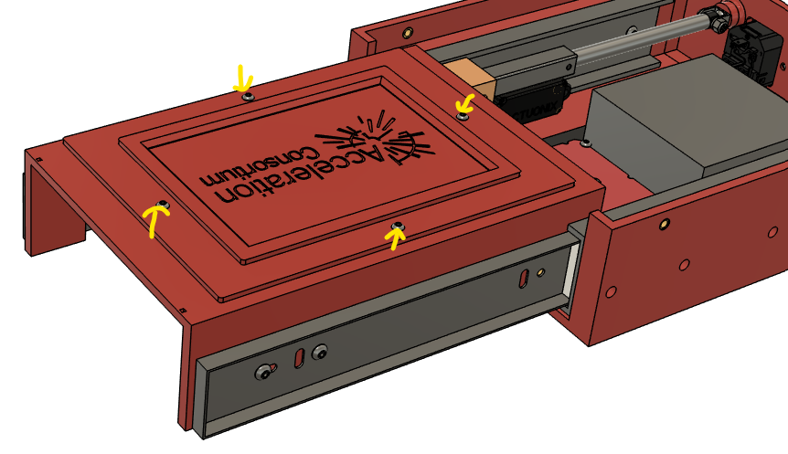
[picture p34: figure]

38. If mounting to a base (in this case, it’s an M6 breadboard, fasten the outer base [1X C5] into the base table. In this case, M6 screws are used [not in BOM, example part # is 9X 92095A234 from McMaster Carr].
39. Install this current assembly into the outer base [1X C5]. Secure with M4x10mm screws [4X B10].

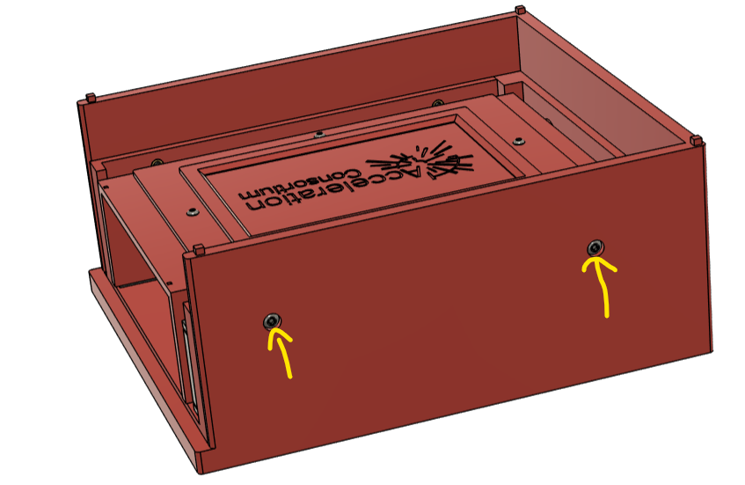
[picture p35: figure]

40. Glue the shield [1X C6] to the well plate tray as shown below.

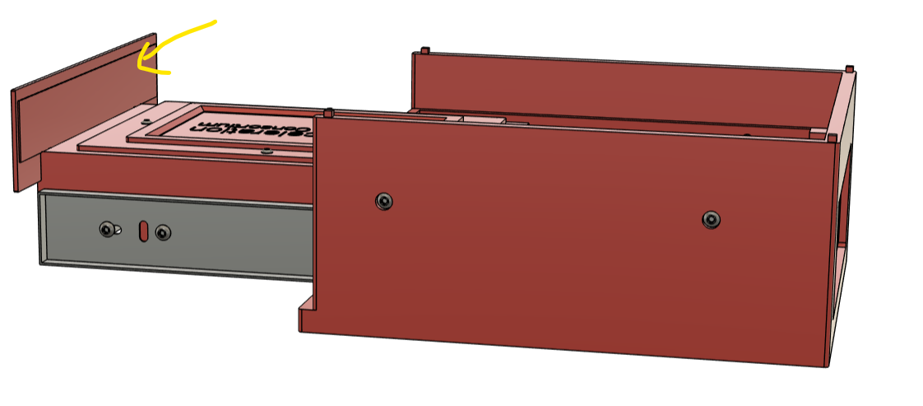
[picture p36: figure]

41. Snap the base lid [1X C7] to the top of the outer base.
42. Place the UV lamp [1X B16] onto the lid. Connect the lamp’s power cord to the receptacle dangling from the back connector panel [cable E1].

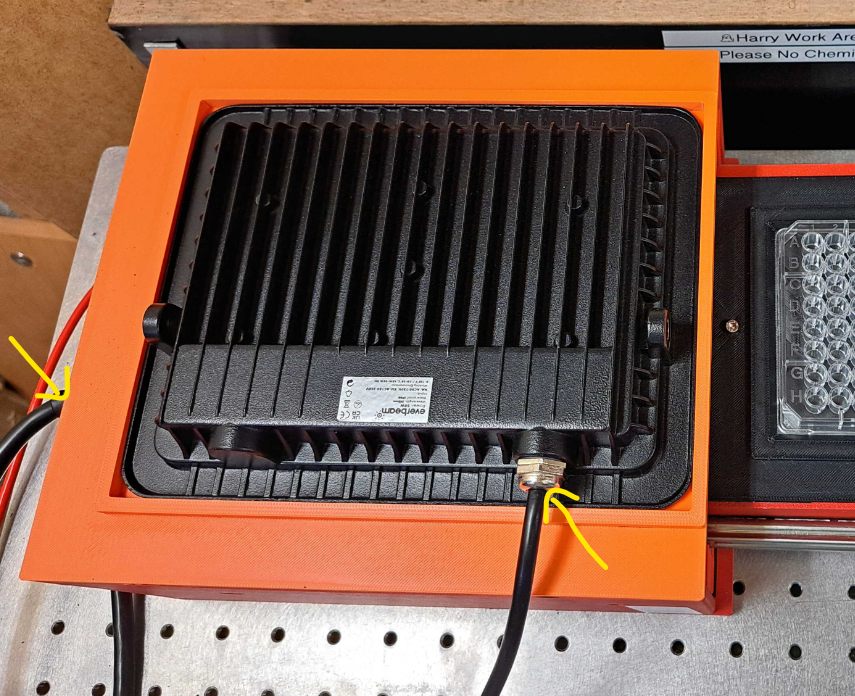
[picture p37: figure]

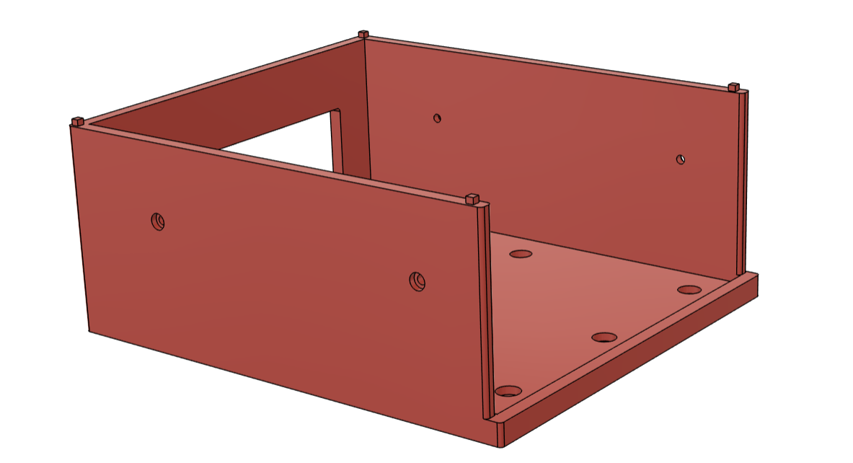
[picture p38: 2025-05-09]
mechanical/3D prints and CAD files/png/uv outer base RevA.png

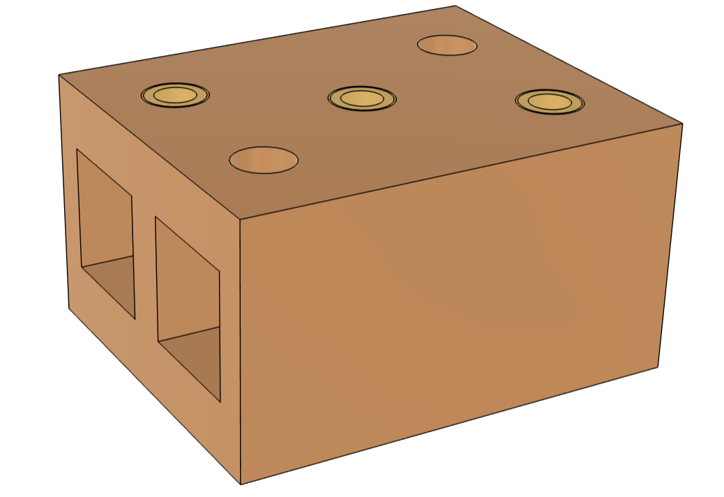
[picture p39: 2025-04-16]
mechanical/3D prints and CAD files/png/actuator bracket RevA.png

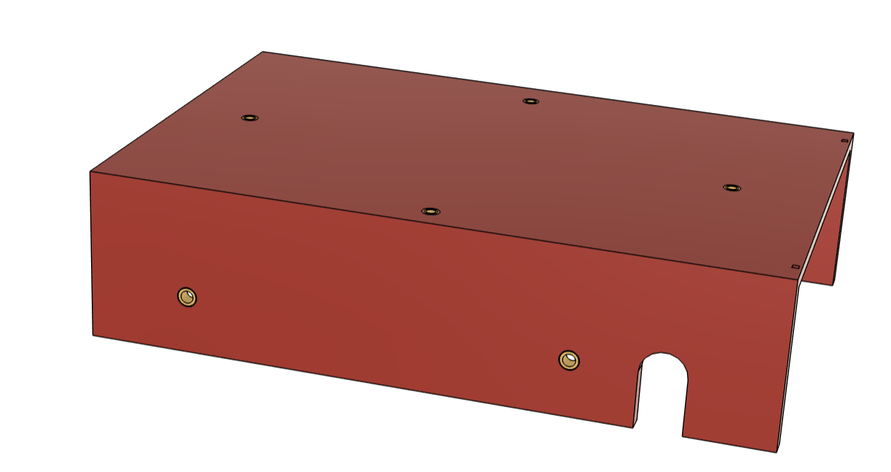
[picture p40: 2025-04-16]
mechanical/3D prints and CAD files/png/tray RevA.png

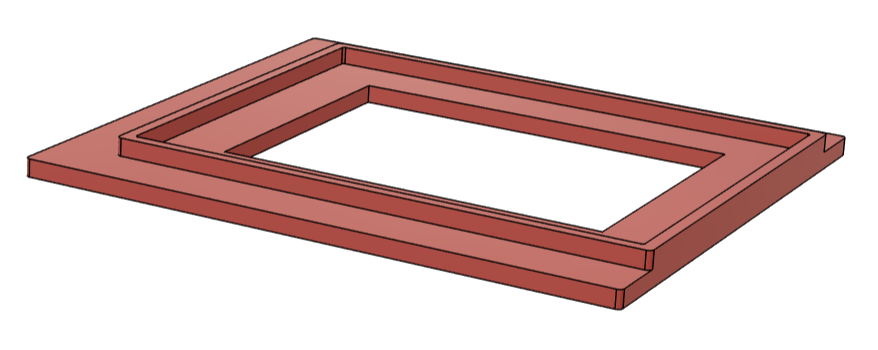
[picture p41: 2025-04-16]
mechanical/3D prints and CAD files/png/uv base lid RevA.png

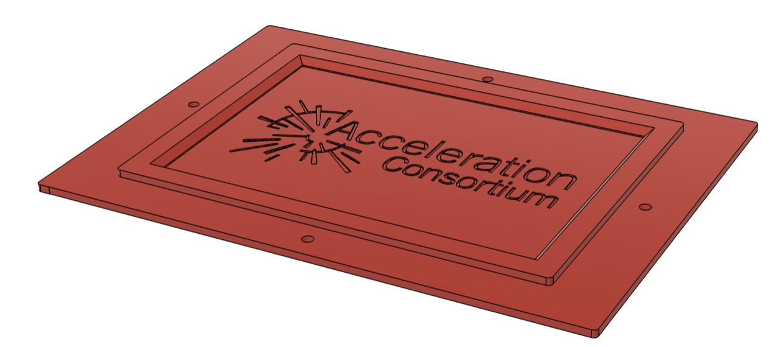
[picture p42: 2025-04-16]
mechanical/3D prints and CAD files/png/tray insert RevA.png

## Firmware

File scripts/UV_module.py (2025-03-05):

from machine import Pin
import time

    
def move_wellplate_out(): 
    track_relay = Pin(27, Pin.OUT)  # GPIO 27 for the track relay
    led = Pin('LED', Pin.OUT)  # Onboard LED for status indication
     
    print("Moving wellplate out")
    track_relay.value(1) # Turn on the track relay
    led.value(1)  # Turn on onboard LED as an indicator
    time.sleep(7)  # Delay for 7 seconds (need time for tray to move in)
    

def move_wellplate_in():
    track_relay = Pin(27, Pin.OUT)  # GPIO 27 for the track relay
    led = Pin('LED', Pin.OUT) 
    
    print("Moving wellplate in")
    track_relay.value(0) # Turn off the track relay
    led.value(0)
    time.sleep(7)  # Delay for 7 seconds (need time for tray to move out)
    
def turn_on_UV(duration): #duration in minutes
    """
    Turns on relay for UV lamp for the specified duration of time (in minutes) & turns the lamp off after the duration is complete.
    """
    lamp_relay = Pin(26, Pin.OUT)  # GPIO 26 for the lamp relay
    led = Pin('LED', Pin.OUT)  # Onboard LED for status indication
    
    duration_seconds = duration*60
    print(f"Turning on lamp for {duration} minutes")
    lamp_relay.value(1)
    led.value(1)
    time.sleep(duration_seconds)  # Delay for duration in seconds
    
    # Turn off the lamp relay after duration is over
    lamp_relay.value(0)
    led.value(0)
    print("UV Lamp turned off")
    time.sleep(1)  # Delay for 1 second to ensure light is off (maybe not needed)
  
# to run methods  
#move_wellplate_out()
#move_wellplate_in()
#turn_on_UV(0.2)
#move_wellplate_out()



### old (archived) methods:
"""
def initialize_crosslinker(): 
    # Set up GPIO pins
    lamp_relay = Pin(26, Pin.OUT)  # GPIO 26 for the lamp relay
    track_relay = Pin(27, Pin.OUT)  # GPIO 27 for the track relay
    led = Pin('LED', Pin.OUT)  # Onboard LED for status indication

    # Ensure relays are initially off
    #lamp_relay.value(0)
    #track_relay.value(0)
    led.value(0)
    print("Initialization complete")
    return track_relay, lamp_relay, led 
"""

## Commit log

2025-03-03 Added additional 3D printing files and code for using the module
    [casing_base.stl, casing_lamp_holder.stl, moving_tray.stl, moving_tray_safety_flap.stl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]
2025-03-05 restructured files into two submodules. added initial well plate track CAD files
    well plate track is just the base with the actuator. UV lamp integration is the addition of the lamp housing, shield, updated tray.
    Will eventually merge these two into the one complete module when finalized.
    [actuator bracket.stl, actuator_bracket v26.step, back connector panel v30.step, back connector panel.stl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]
2025-03-05 added some electrical tests
    will need to continue updating
    [electrical test BOM.xlsx]
2025-04-14 updated folder structure
    moved some things offline, will upload build instructions soon
    [actuator bracket.stl, actuator_bracket v26.step, assembly_well plate track v43.f3z, assembly_well plate track v44.step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]
2025-04-15 updated electrical test folder
    this part should be done hopefully
    [electrical test BOM.xlsx, electronics mounting plate v35.step]
2025-04-16 updated cad and bom
    started readme for assembly instructions
    [actuator bracket RevA.step, actuator bracket RevA.stl, actuator bracket.stl, assembly_the_cure_RevA.f3z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]
2025-04-16 Update README.md
    added 3d printed pictures in bom?
2025-04-17 started draft assembly instructiosn
2025-04-19 updated assembly instructions
    [the cure BOM RevA 2025-04-15.xlsx]
2025-04-20 i think the documentation is pretty much complete
    probably need to fine tune the readme and docx
    [actuator bracket RevA.step, assembly_the_cure RevA 2025-04-20.f3z, assembly_the_cure_RevA.f3z, the cure - BOM RevA 2025-04-20.xlsx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]
2025-05-09 Update README.md
    corrected typos and C1/C6 heat sets.
    updated image for C5
2025-05-09 Update README.md
    c6 no heat sets
2025-05-09 update assembly instrucitons
    per monique's comments. mounting to breadboard and modifying images for the outer base
2025-05-09 updated cad files
    [assembly_the_cure RevA 2025-04-20.f3z, assembly_the_cure RevA 2025-05-09.f3z, uv outer base RevA.step, uv outer base RevA.stl]
